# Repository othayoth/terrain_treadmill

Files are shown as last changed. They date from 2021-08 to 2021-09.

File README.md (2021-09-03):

# Terrain Treadmill 
This repository contains code being used to run the complex terrain treadmill in the [Terradynamics Lab](https://li.me.jhu.edu/) at Johns Hopkins University and accompanies publication ['A terrain treadmill to study small animal locomotion through large obstacles'](https://doi.org/10.1101/2021.08.31.458392)

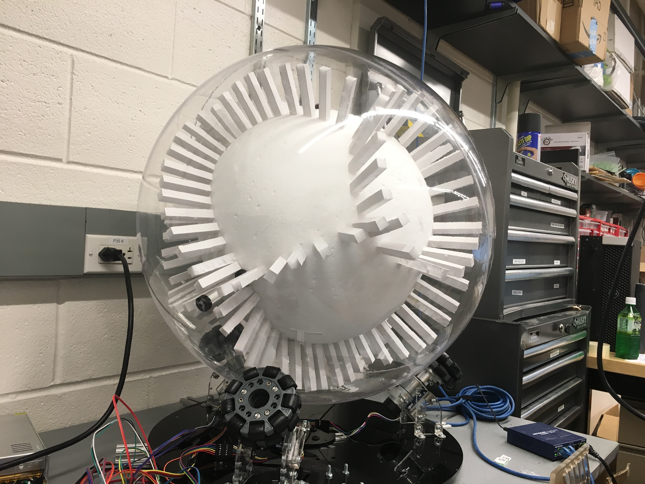
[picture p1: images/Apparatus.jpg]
Apparatus apparatus image


## Project Description
The purpose of this project was to develop a novel terrain treadmill to study Animal-Terrain Interaction During Locomotion in Complex Environments. This device allows for detailed study of cockroach dynamics and behavior over over large spatiotemporal scales.

### Table of Contents

* [Overview and Setup](#terrain-treadmill)
    * [Device Overview](#device-overview)
	* [Installation Instructions](#installation-instructions)
	* [Running the Device](#running-the-device)
	* [Device Tuning](#device-tuning)
  * [Data Analysis](#data-analysis)
	* [Maintenance](#maintenance)
	* [Parts List](#parts-list)
* [Nodes](./src#nodes)
* [Launch Files](./launch#launch-files)
* [Arduino Code](./Arduino#arduino-code)

## Device Overview

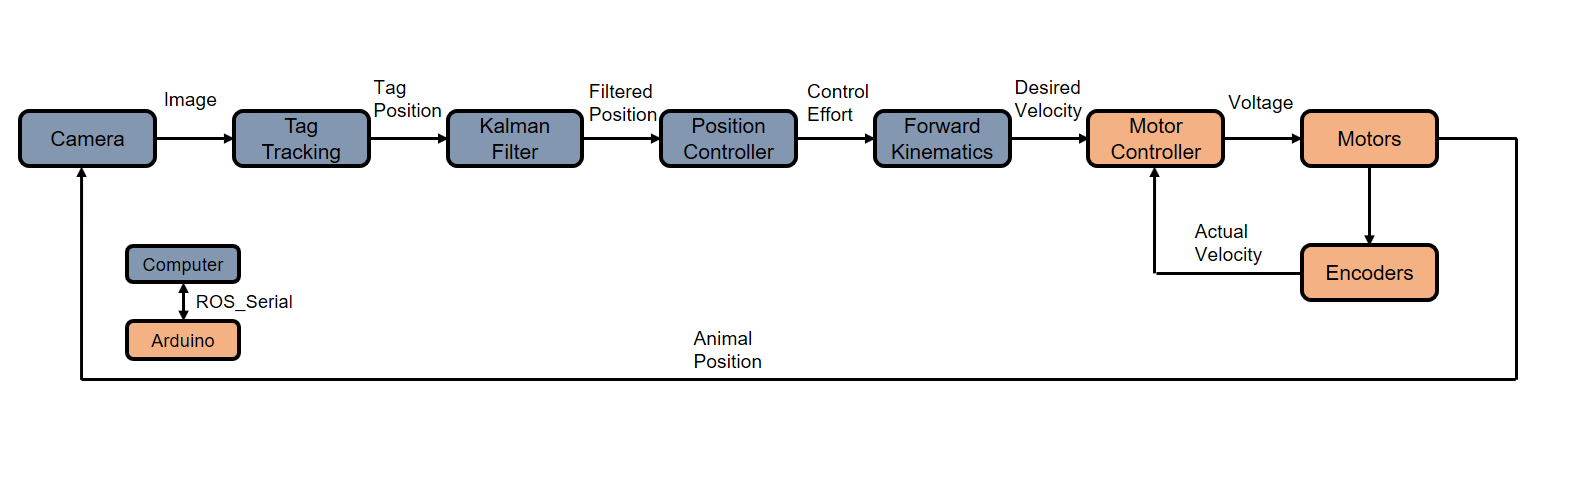
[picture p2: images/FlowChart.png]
FlowChart device flow chart

The terrain treadmill consists of two concentric spheres rigidly attached together. The animal moves through interchangeable terrain modules mounted on the inner sphere, and the transparent outer sphere allows its position to be tracked in real time. This information is then used to actuate the spheres via close-loop control, so that they rotate in the opposite direction in order to keep the animal on top.

The device uses a computer running ROS Indigo for image processing, filtering, and control. An Arduino is used to control the motors which actuate the device. To learn more about the ROS nodes being used to control the device, see the [node](./src) section. To learn more about the Arduino code, see the [Arduino](./Arduino) section.

## Installation Instructions
### ROS Package Install

First, make sure that ROS is installed and that you have a properly configured catkin [workspace](http://wiki.ros.org/catkin/Tutorials/create_a_workspace). Clone this project into your workspace using:
* `git clone git@github.com:TerradynamicsLab/terrain_treadmill.git`

This repository also has several dependencies on packages not yet released on `apt-get`. Install these packages using the same method as above:
* [aruco_ros](https://github.com/pal-robotics/aruco_ros): minimum version required 0.2.2
* [camera_base](https://github.com/KumarRobotics/camera_base)
* [flea3](https://github.com/KumarRobotics/flea3)

The remaining dependencies are listed in [CMakeLists.txt](./CMakeLists.txt) and can be installed normally using `apt-get`. Source the workspace `source devel/setup.bash` and make the package `catkin_make` to build the project.

### Hardware setup
An [Arduino Due](https://store.arduino.cc/usa/arduino-due) is used to interface with the three [DC Motors](https://www.pololu.com/product/2826) used to actuate the device. A circuit diagram for the project can be found [here](./images/Circuit.pdf). This repository contains the necessary libraries to compile to main [terrain_treadmill.ino](./Arduino/terrain_treadmill/terrain_treadmill.ino) sketch and upload it to the Arduino. Copy the [pid_lib](./Arduino/Libraries/pid_lib) and [ros_lib](./Arduino/Libraries/ros_lib) (generated using [rosserial](http://wiki.ros.org/rosserial)) libraries into your Arduino libraries folder. Then compile and upload `terrain_treadmill.ino` onto the device.

* Note: if you have trouble compiling the Arduino Code, see the Arduino [readme](./Arduino).

## Running the Device
To start the device, navigate to your workspace, source the correct environment variables, and launch [start.launch](./launch/start.launch)
* `cd [catkin_ws]`
* `source devel/setup.bash`
* `roslaunch terrain_treadmill start.launch`

This will start the device with the default settings. [Rqt](http://wiki.ros.org/rqt) is used for real-time data analysis and debugging.

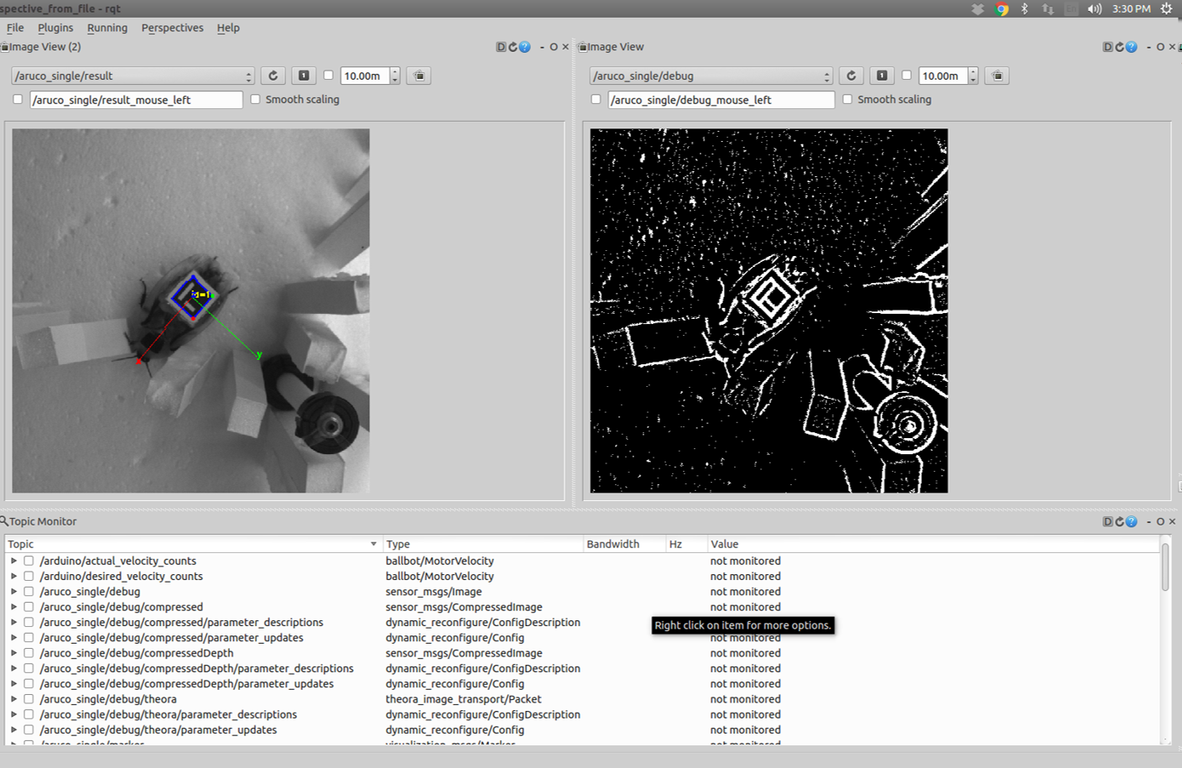
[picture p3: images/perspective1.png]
rqt1 rqt perspective 1


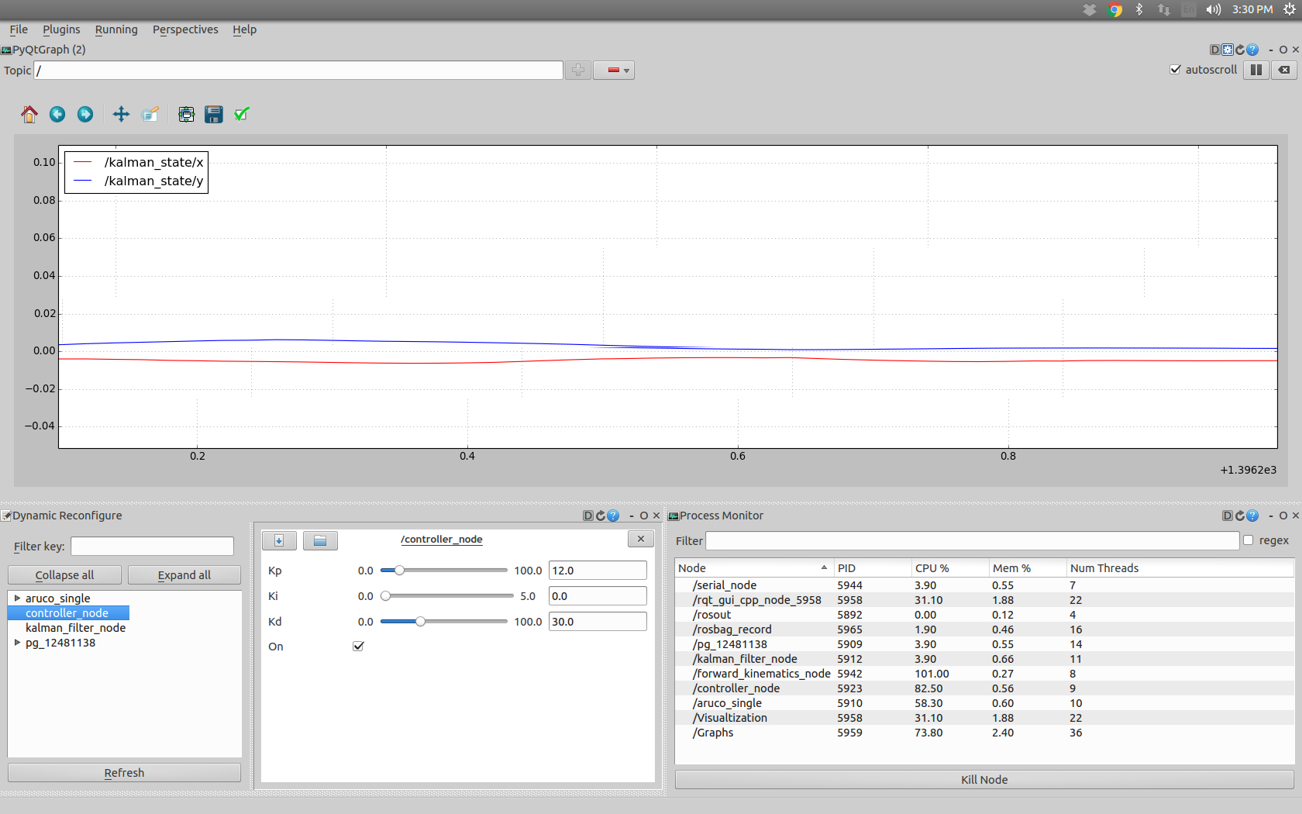
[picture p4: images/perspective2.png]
rqt2 rqt perspective 2


Various properties can be altered by specifying arguments at runtime. For example:
* `roslaunch terrain_treadmill start.launch record:=true`: records specified topics into a .bag file which is saved in the ~/.ros directory
* `roslaunch terrain_treadmill start.launch visualization:=false light_visualizations:=true`: starts the project in light visualization mode which hides debugging information

For more options, see [launch](./launch).

## Device Tuning

Tracking_Demo tracking demo

Several aspects of the device must be tuned in order to achieve optimum performance. These include:
* Low-Level Motor Controllers:
The Arduino uses three [PID Controllers](https://en.wikipedia.org/wiki/PID_controller) to match the desired velocity sent to the Arduino from the computer. These controllers are tuned to track the desired velocity as closely as possible while maintaining desired response characteristics (low overshoot, quick settling time, etc.). The [motor_test_node.py](./src/motor_test_node.py) node can be used to aid in the tuning of these controllers. See the [node readme](./src) for more information.

* Kalman Filter Gains:
A constant velocity model [kalman filter](https://en.wikipedia.org/wiki/Kalman_filter) is used to estimate the animal position when the tracking data becomes temporarily unavailable. Several aspects of the filter must be tuned for optimal performance. For this project, the most relevant parameter is the process covariance which can be tuned using dynamic reconfigure. For more information on the kalman filter, see the [node readme](./src).

* High-Level Controller:
A PID position controller is used to determine the desired control effort as a result of the animal's deviation from the center of the image frame. The PID gains from this controller can be tuned using dynamic reconfigure. For more information on this controller, see the [node readme](./src).

* Camera parameters:
Various camera parameters must be tuned in order to obtain good images for tracking. Camera placement, focus, lens size, and aperture are all hardware adjustments for this setup. Additionally, there are several parameters which can be adjusted in [flea3.launch](./launch/flea3.launch). These parameters can be tuned using dynamic reconfigure and then saved using the launch file.

  * Frame-rate: dictates how quickly the camera captures images. Note, higher frame rates do not necessarily result in better performance if Aruco tag detection cannot analyze images quickly enough. It is recommended to match the frame-rate to the frequency of Aruco tag detection at a given resolution.

  * Resolution: dictates the computational cost for Aruco tag detection. The smallest resolution that satisfies the other requirements is recommended. Aruco tag detection can be performed at ~50 Hz using a 688 x 700 image.

  * Shutter-Time: dictates how long shutter stays open for each image capture. Keep shutter-time low to reduce motion blur and improve tag detection. For this setup, a 5 ms shutter time produces good results.

  * For more information on tuning camera parameters, see [Guide to photography](https://i.redd.it/tq0zowda2shz.jpg).

  * Before use, the camera will also need to be calibrated to account for distortion. For information on how to calibrate the camera, see the [launch readme](./launch).

* Aruco Tracking Parameters:
[Aruco](https://www.uco.es/investiga/grupos/ava/node/26) is a tracking library which uses VR tags to determine tag locations in real-world coordinates. [Pal Robotics ROS implementation](https://github.com/pal-robotics/aruco_ros) of the library is used for this project. Assuming the camera parameters are set properly, there are several Aruco parameters which also must be adjusted for optimal performance. First, the markerID and size must be properly set in [aruco_marker_finder.launch](./launch/aruco_marker_finder.launch). The threshold parameters can then be adjusted using dynamic reconfigure. To permanently save adjustments, change the default values within your aruco_ros ArucoThreshold.cfg file. Note: this file is not located in the terrain_treadmill package.

## Data Analysis
Data can be recorded in a [rosbag](http://wiki.ros.org/rosbag) by running `roslaunch terrain_treadmill start.launch record:=true.` This results in a rosbag file containing being stored in your `~/.ros` directory. This bag can be played back for analysis. For more information on using rosbag to play back data, see [here](http://wiki.ros.org/rosbag/Commandline#play). Videos recorded in rosbag files can also be exported in your desired format. For information on exporting rosbag videos, see [here](http://wiki.ros.org/rosbag/Tutorials/Exporting%20image%20and%20video%20data). Rosbag files can also be imported directly to MATLAB using the [Robotics Systems Toolbox](https://www.mathworks.com/help/robotics/index.html). This package contains custom messages which will need to be imported to MATLAB using the [rosgenmsg](https://www.mathworks.com/help/robotics/ref/rosgenmsg.html) function which requires the [Robotics System Toolbox Interface for ROS Custom Messages](https://www.mathworks.com/matlabcentral/fileexchange/49810-robotics-system-toolbox-interface-for-ros-custom-messages).

## Maintenance
Acrylic hemispheres quickly build up finger prints, scuff marks, small scratches, and tape residue during normal use. DO NOT clean acrylic with regular towels. Use microfiber clothes to avoid scratching the surface. Use [acrylic cleaner](https://www.amazon.com/NOVUS-7100-Plastic-Polish-Kit/dp/B002UCYRZU) to help remove finger prints, dirt, and small scratches. Use [WD-40](https://www.amazon.com/WD-40-Multi-Use-Product-Multi-Purpose-Lubricant/dp/B0083V8H0I/ref=sr_1_1?s=automotive&ie=UTF8&qid=1504127919&sr=1-1&keywords=wd-40) to aid in the removal of tape residue.

## Parts List
* 1x [Arduino Due](https://store.arduino.cc/usa/arduino-due)
* 3x [DC Motor + Encoder](https://www.pololu.com/product/2826)
* 3x [DC Motor Driver](https://www.amazon.com/SainSmart-Stepper-Controller-Mega2560-Duemilanove/dp/B00AJGM37I)
* 1x [12V Power Supply](https://www.amazon.com/eTopxizu-Universal-Regulated-Switching-Computer/dp/B00D7CWSCG)
* 2x 24" Optically Clear Acrylic Hemisphere
* 1x 16" Styrofoam Ball
* 1x Tapped Plastic Rod + 2x screws
* 1x [Pointgrey Flea3 Camera](https://www.ptgrey.com/flea3-usb3-vision-cameras)
* 1x [16 mm lens](http://www.fujifilmusa.com/products/optical_devices/machine-vision/1-15-mp/cf16ha-1/)

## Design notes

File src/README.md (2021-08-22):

# Nodes

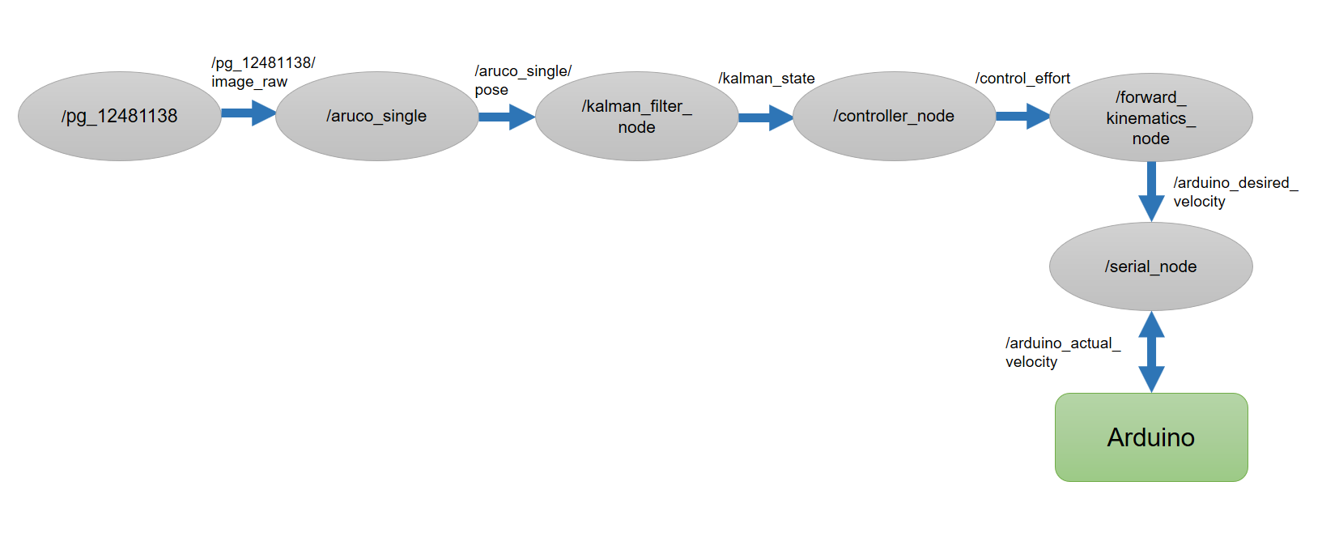
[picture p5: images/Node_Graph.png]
node graph simplified node graph


### Table of Contents
* [Overview and Setup](https://github.com/TerradynamicsLab/terrain_treadmill#terrain-treadmill)
* [Nodes](#nodes)
	* [/pg_12481138](#pg_12481138)
	* [aruco_single](#aruco_single)
	* [kalman_filter_node](#kalman_filter_node)
		* [tag_marker](#tag_marker)
		* [filter_marker](#filter_marker)
		* [tuning](#tuning)
	* [controller_node](#controller_node)
	* [forward_kinematics_node](#forward_kinematics_node)
	* [serial_node](#serial_node)
	* [motor_test_node](#motor_test_node)
* [Launch Files](../launch#launch-files)
* [Arduino Code](../Arduino#arduino-code)

## pg_12481138
This node publishes data from the camera used to track the Aruco tag located on the animal. It is started by [flea3.launch](../launch/flea3.launch). This node publishes several topics, the most relevant topics are:
* `/pg_12481138/camera_info` contains camera calibration data. It is used by the `aruco_single` node to convert tag position from pixels into real-world coordinates.
* `/pg_12481138/image_raw` contains the raw images output by the camera.
* `/pg_12481138/image_raw/compressed` contains compressed images output by the camera. Recording compressed images rather than raw images using rosbag results in smaller file sizes. Generally, all image topics in this package contain a corresponding compressed version. To view this topic using image_view, use: `rosrun image_view image_view image:=/pg_12481138/image_raw compressed`.

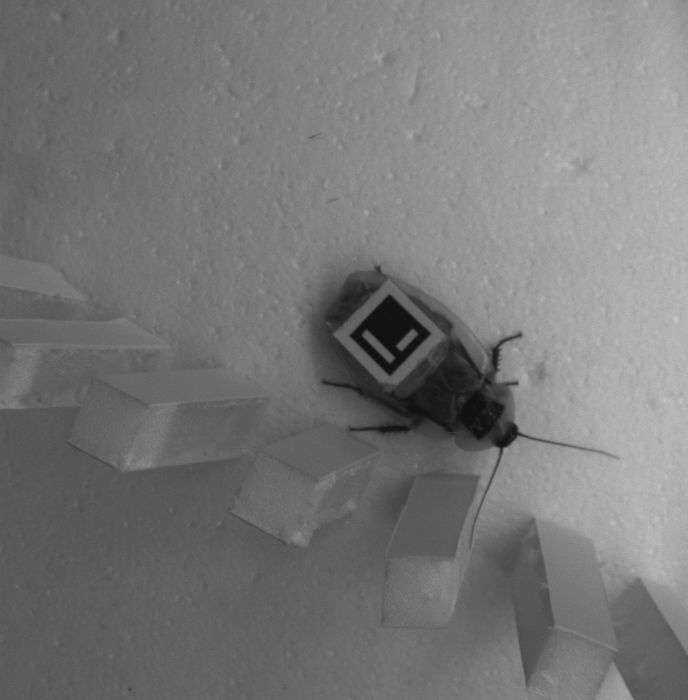
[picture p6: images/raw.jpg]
image_raw /pg_12481138/image_raw


## aruco_single
This node performs Aruco tag tracking. It is started by [aruco_marker_finder.launch](../launch/aruco_marker_finder.launch) It subscribes to `/pg_12481138/image_raw` and `/pg_12481138/camera_info` and uses this data to detect the tag position and convert it to real-world coordinates. This node publishes several useful topics:
* `/aruco_single/pose` contains position and orientation of Aruco tag using [geometry_msgs/Pose](http://docs.ros.org/api/geometry_msgs/html/msg/Pose.html) message.
* `/aruco_single/result` contains image displaying tag tracking result. Useful for tuning tracking and camera parameters.

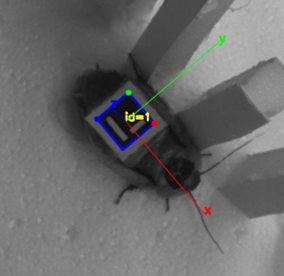
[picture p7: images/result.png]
result /aruco_single/result


* `/aruco_single/debug` contains binary image displaying result of image thresholding performed Aruco node. This image is used to tune the Aruco parameters discussed [here](https://github.com/TerradynamicsLab/terrain_treadmill#device-tuning).

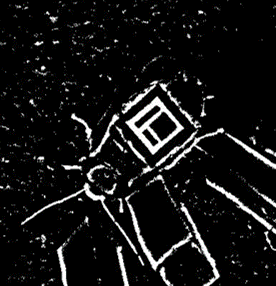
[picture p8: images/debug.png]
debug /aruco_single/debug


## kalman_filter_node
[kalman_filter_node.py](./kalman_filter_node.py) filters noisy position data from Aruco tag tracking. Furthermore, this node is used to predict tag location when the tag is temporarily obscured by obstacles. This makes the apparatus more reliable and less-prone to sudden impulses when tracking is inconsistent. This node is a constant velocity Kalman filter. To learn more about Kalman filters, start [here](https://en.wikipedia.org/wiki/Kalman_filter).

The node subscribes to the `aruco_single/pose` topic, performs filtering, and publishes the `kalman_state` topic at a [fixed frequency](./kalman_filter_node.py#L48) regardless of camera frame-rate. The filter first predicts a new state using previous state information and a constant velocity kinematic model.

```python

# Time Update (Prediction)
# ========================
# Project the state ahead
self.x = self.F*self.x

# Project the error covariance ahead
self.P = self.F*self.P*self.F.T + self.Q								

```

 Then, if new state information has been determined by the Aruco tracking node, it performs a correction (measurement) in which it uses measurement information to obtain a more accurate guess of the tag state as well as to influence future predictions.

```python
# Measurement Update (Correction)
# ===============================
# Compute the Kalman Gain
S = self.H*self.P*self.H.T + self.R
K = (self.P*self.H.T) * np.linalg.pinv(S)

# Update the estimate via z
Z = np.matrix([[self.posex, self.posey, self.yaw]]).T
y = Z - (self.H*self.x)
self.x = self.x + (K*y)

# Update the error covariance
self.P = (self.I - (K*self.H)) *self.P

 ```

 If no measurement information is available, it continues performing predictions until a limit is reached. After this limit, it uses measurements of zero to halt the apparatus motion until Aruco tracking information becomes available.

 ```python

 if self.missed_frames > 15:
 				##  Use zero as the measurement
 				self.posex = 0
 				self.posey = 0
 				self.yaw = 0

 				# Compute the Kalman Gain
 				S = self.H*self.P*self.H.T + self.R
 				K = (self.P*self.H.T) * np.linalg.pinv(S)

 				# Update the estimate via z
 				Z = np.matrix([[self.posex, self.posey, self.yaw]]).T
 				y = Z - (self.H*self.x)
 				self.x = self.x + (K*y)

 				# Update the error covariance
 				self.P = (self.I - (K*self.H)) *self.P

 ```

 The filter's process covariance can be tuned using rqt_reconfigure to alter the sensitivity to new measurements. The tag_marker and filter_marker nodes discussed below can be helpful in tuning the filter parameters to obtain the desired response.

 #### tag_marker

 [tag_marker.py](./tag_marker.py) subscribes to Aruco tag information from the `/aruco_single/pose` topic. It uses this data to publish an [Rviz](http://wiki.ros.org/rviz) marker on the `/tag_marker` topic.

 #### filter_marker

 [filter_marker.py](./filter_marker.py) subscribes to filter information on the `/kalman_state` topic. It uses this data to publish an Rviz marker on the `/filter_marker topic`

 #### tuning
[Rviz](http://wiki.ros.org/rviz) is a ROS package useful for data visualization. It subscribes to [Rviz Markers](http://wiki.ros.org/rviz/DisplayTypes/Marker) and displays them in a 3-D environment. These markers can be used to tune the Kalman filter process covariance (or other parameters) using rqt_reconfigure. To start the apparatus in the proper configuration for tuning, set the Rviz argument to true: `roslaunch terrain_treadmill start.launch Rviz:=true`.

[Examples]

## controller_node

[controller_node.py](./controller_node.py) is the high level position PID controller for the device. This node subscribes to the `/kalman_state` topic containing position information about the tag located on the animal body. The 2-D deviation from center (x,y) is used as the error for the controller. The orientation (theta) is not considered. The error is fed into a PID controller and control effort is calculated:

```python
def PID_Controller(self, msg):
    # Calculate Error
    self.Ex = msg.x
    self.Ey = msg.y
    # self.Et = msg.theta

    # Calculate Integral Error
    self.Exint = self.Exint + self.Ex
    self.Eyint = self.Eyint + self.Ey
    # self.Etint = self.Etint + self.Et

    # Calculate Derivative Error
    self.Exdot = self.Ex - self.Exold
    self.Eydot = self.Ey - self.Eyold
    # self.Etdot = self.Et - self.Etold

    # Update Previous Error
    self.Exold = self.Ex
    self.Eyold = self.Ey
    # self.Etold = self.Et

    # Calculate Control Effort
    self.controlEffort.Ux = self.Kp*self.Ex + self.Ki*self.Exint + self.Kd*self.Exdot
    self.controlEffort.Uy = self.Kp*self.Ey + self.Ki*self.Eyint + self.Kd*self.Eydot
    self.controlEffort.Ut = 0.0 #self.Kp*self.Et + self.Ki*self.Etint + self.Kd*self.Etdot
    self.controlEffort.header.stamp = rospy.Time.now()
```

 This control effort is published on the `/control_effort` topic. When the tag is within 3 mm of the center of the frame, no control effort is used. The PID gains are tunable using rqt_reconfigure. The controller can also be turned on/off using rqt_reconfigure.

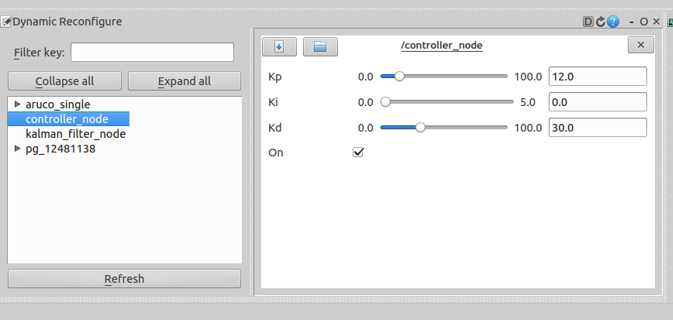
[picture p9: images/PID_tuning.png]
PID Tuning


## forward_kinematics_node

[forward_kinematics_node.py](./forward_kinematics_node.py) subscribes to the `/control_effort` containing real-world control effort information (x, y, theta) and converts this information into the required motor velocities for the three motors which will cause the ball to rotate in the desired trajectory. These velocities are then converted from `rad/s` into `encoder counts/controller interrupt` and published on the `/arduino/desired_velocity_counts` topic.

The forward kinematics for this structure were obtained from this [paper](http://ieeexplore.ieee.org/document/5152324/). They are given by:

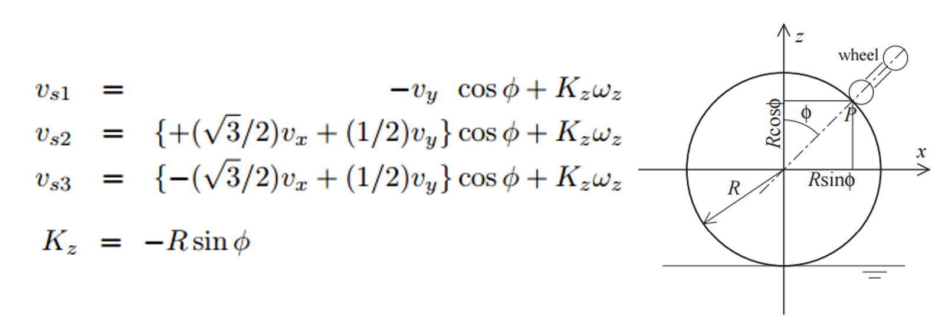
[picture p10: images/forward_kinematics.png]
forward_kinematics


## serial_node

The serial node is started by [serial.launch](../launch/serial.launch). This node is responsible for maintaining communication between ROS and the Arduino. It subscribes to the `/arduino/desired_velocity_counts` topic and sends this data to the Arduino over the computer's serial port. It also receives the `/arduino/actual_velocity_counts` information over the same serial port and publishes this topic.

## motor_test_node

[motor_test_node.py](./motor_test_node.py) can be used to tune the PID controllers being used to control the DC motors. The node uses rqt_reconfigure to send desired velocities to each motor in counts. The desired/actual velocities can be plotted to aid in the tuning of the controllers.
* `rosrun terrain_treadmill motor_test_node.py` to start the node
* `rosrun rqt_reconfigure rqt_reconfigure` to startup rqt_reconfigure
* `rosrun rqt_plot rqt_plot` to start rqt_plot. Add `/arduino/actual_velocity_counts` and `/arduino/desired_velocity_counts` and then configure to visualize results

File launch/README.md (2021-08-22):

# Launch Files

### Table of Contents

* [Overview and Setup](../#terrain-treadmill)
* [Nodes](../src#nodes)
* [Launch Files](#launch-files)
	* [start](#start)
	* [aruco_marker_finder](#aruco_marker_finder)
	* [flea3](#flea3)
	* [serial](#serial)
* [Arduino Code](../Arduino#arduino-code)

## start
[start.launch](./start.launch) is used to startup the entire apparatus. This launch file allows the apparatus to be started without certain nodes for debugging purposes (see launch file for options).

The file can also be used to setup data collection for the device. Setting the `record` arg to true causes a rosbag to be recorded. By default, this file will be saved in the `~/.ros` directory. To change which topics are recorded, add or delete them from the [arguments list](./start.launch#L68-L69).

For more information on using rosbag, see the [package documentation](http://wiki.ros.org/rosbag). For more information on using rosbag to playback data using command-line arguments, see [here](http://wiki.ros.org/rosbag/Commandline).

## aruco_marker_finder
[aruco_marker_finder.launch](./aruco_marker_finder.launch) is used to start the [simple_single](https://github.com/pal-robotics/aruco_ros/blob/indigo-devel/aruco_ros/src/simple_single.cpp) node from the [aruco_ros package](https://github.com/pal-robotics/aruco_ros)  with the proper settings for tag detection. Before using, this launch file confirm that:
* The [markerId](./aruco_marker_finder.launch#L3) is properly specified. To generate new markers, modify [this url](http://terpconnect.umd.edu/~jwelsh12/enes100/marker.html?id=1&size_mm=70&padding_mm=5).
* The [markerSize](./aruco_marker_finder.launch#L4) has been measured and specified.
* The [camera topics](./aruco_marker_finder.launch#L11-L12) have been properly remapped.

## flea3
[flea3.launch](./flea3.launch) is used to start a Point Grey [Flea3 camera](https://www.ptgrey.com/support/downloads/10120) using the [flea3_single_node](https://github.com/KumarRobotics/flea3/tree/master/src/single) from the [flea3](https://github.com/KumarRobotics/flea3/tree/master/src) package. This launch file allows the camera parameters to be set to desired values. Camera tuning is disucssed in the main package [readme](../README.md#terrain-treadmill). After tuning, this launch file can also be used to calibrate the camera. Print out a [calibration board](http://wiki.ros.org/camera_calibration/Tutorials/MonocularCalibration?action=AttachFile&do=view&target=check-108.pdf) and measure the size of one of the squares. Then, calibrate the camera by running:
* `roslaunch terrain_treadmill flea3.launch calib:=true size:=8x6 square:=[measured square size]`

After, overwrite the old [calibration file](../config/camera.yaml) with your new calibration. For more information on using ROS to calibrate your camera, see the [camera_calibration](http://wiki.ros.org/camera_calibration/Tutorials/MonocularCalibration) package.

## serial
[serial.launch](./serial.launch) is used to start a serial communication stream between ROS and the Arduino. In order to start the serial stream, the serial [port](./serial.launch#L3) and [baud](./serial.launch#L4) must be properly specified. Specifically, the baud must match the [Arduino](../Arduino/terrain_treadmill/terrain_treadmill.ino#L12). Note, for the Arduino Due, the max serial rate is `115200`, but the default rate has proven to be more reliable. If higher serial rates are required, consider switching to a different microcontroller or communication protocol.

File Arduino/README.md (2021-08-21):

# Arduino Code

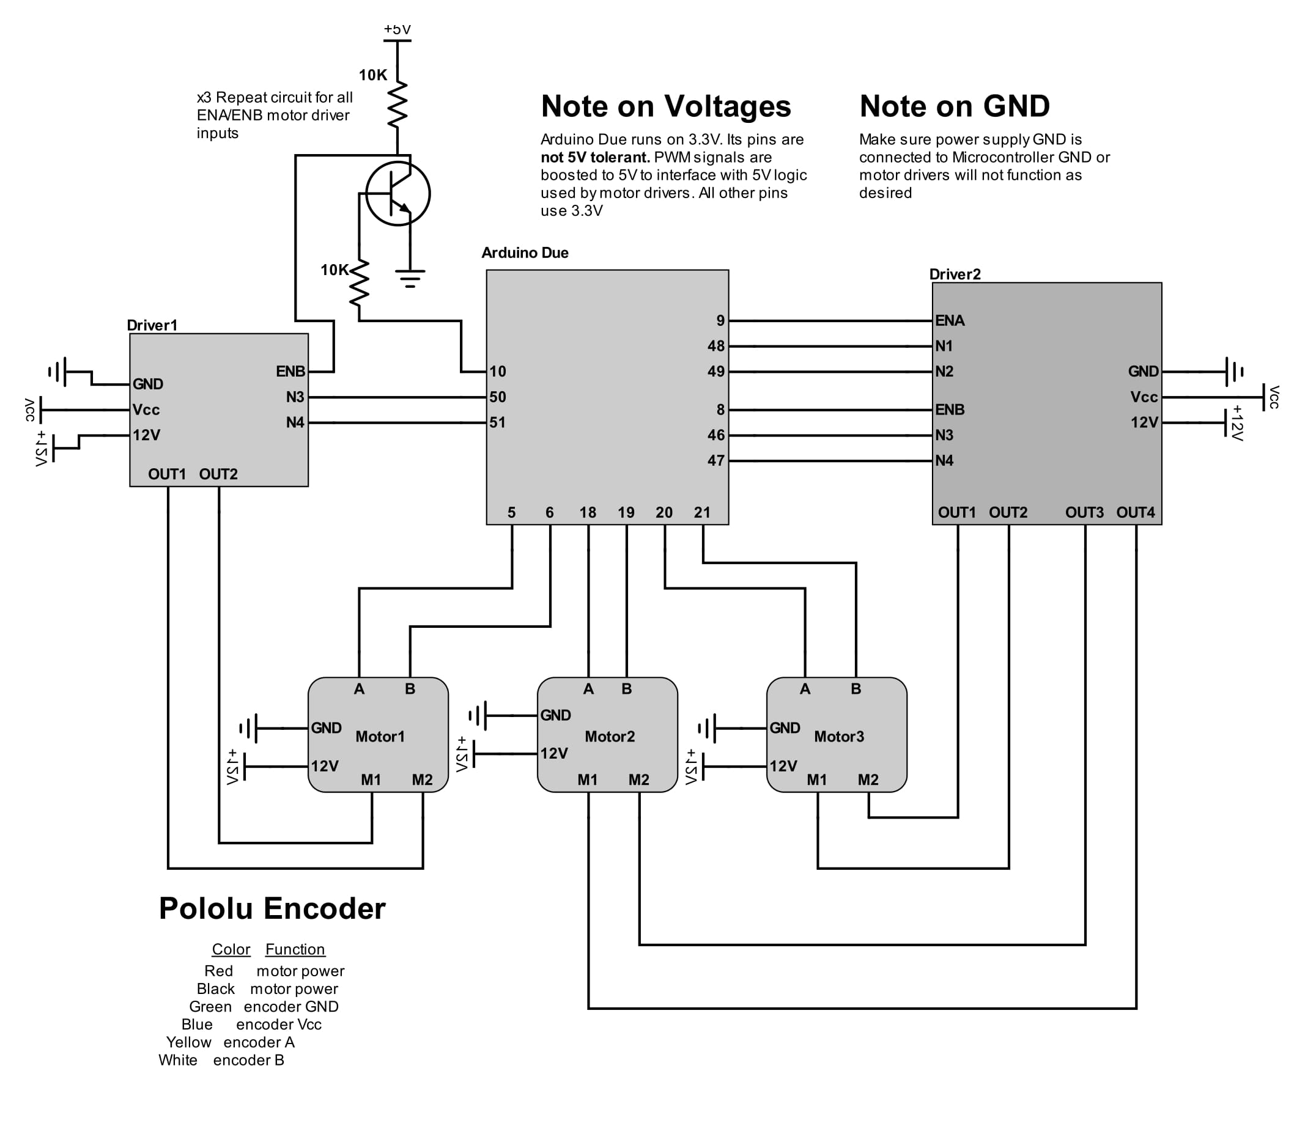
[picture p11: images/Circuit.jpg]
circuit diagram


### Table of Contents

* [Overview and Setup](#terrain-treadmill)
* [Nodes](../src#nodes)
* [Launch Files](../launch#launch-files)
* [Arduino Code](#arduino-code)
	* [Main](#main)
	* [Libraries](#libraries)
	    * [ROS Interface Library](#ros-interface-library)
	    * [Motor Control Library](#motor-control-library)
	    	* [Encoder](#encoder)
	    	* [Controller](#controller)
	    	* [Motors](#motors)
	    	* [Utilities](#utilities)
	    	* [Timer](#timer)

## Main

[terrain_treadmill.ino](./terrain_treadmill/terrain_treadmill.ino) is the main sketch running on the Arduino. It sets up ROS Communication, initializes the motor controllers, and receives/sends desired/actual motor velocities to ROS.

## Libraries

### ROS Interface Library
[ros_lib](./Libraries/ros_lib) contains the files required to use [rosserial](http://wiki.ros.org/rosserial) to communicate with the Arduino. If you're having trouble getting the sketch to compile after following the instructions in [Hardware setup](), try reinstalling ros_lib in your Arduino sketchbook by sourcing your workspace and then [Install ros_lib into the Arduino Environment](http://wiki.ros.org/rosserial_arduino/Tutorials/Arduino%20IDE%20Setup). NOTE, when using this library with an Arduino Due, manually change `Serial1` to `Serial` in [ArduinoHardware.h](./Libraries/ros_lib/ArduinoHardware.h#L68) or the Arduino will not connect with ROS.

### Motor Control Library
[pid_lib](./Libraries/pid_lib) is a custom C library for velocity control of 3 DC motors with encoders using PID control. The library files are organized as follows. For more information on an individual file, check the comments. This library can easily be adapted to use more/less motors or different hardware.

#### Encoder

[Encoder.cpp](./Libraries/pid_lib/Encoder.cpp), [Encoder.h](./Libraries/pid_lib/Encoder.h)

These files contain the functions which are used to interpret the quadrature encoder waveforms to determine motor position and velocity. The encoder signals cause rising-edge interrupts on the Arduino. The [interrupt service routines](./Libraries/pid_lib/Encoder.cpp#L216-L298) then add/subtract counts to the position totals. For this implementation, the full resolution of the encoder is not utilized in interest of simplifying the computational cost. Therefore, the total encoder resolution should be divided by four to obtain the actual resolution. The [filtered_velocity](./Libraries/pid_lib/Encoder.cpp#L193-L214) function uses a moving average of size n (set in [terrain_treadmill.ino](./terrain_treadmill/terrain_treadmill.ino#L22)) to get a less noisy estimate of the velocity at any time.  

#### Controller

[Controller.cpp](./Libraries/pid_lib/Controller.cpp), [Controller.h](./Libraries/pid_lib/Controller.h)

These files contain the fixed frequency PID controller used to control the motors to match their desired velocities. A [timer based interrpt](./Libraries/pid_lib/Controller.cpp#L26) is used to trigger the controller to update motor voltages at a fixed frequency. The actual positions/velocities are [read](./Libraries/pid_lib/Controller.cpp#L46-L48) by the controller and [compared](./Libraries/pid_lib/Controller.cpp#L50-L52) to the desired values. Then, the controller determines the [desired effort](./Libraries/pid_lib/Controller.cpp#L142-L146) based on the error between the two. If the effort is negative, the motor direction is [flipped](./Libraries/pid_lib/Controller.cpp#L166-L174). Max control effort corresponds with a [full byte](./Libraries/pid_lib/Controller.cpp#L177-L180) (255).

#### Motors

[Motors.cpp](./Libraries/pid_lib/Motors.cpp), [Motors.h](./Libraries/pid_lib/Motors.h)

These files contain the necessary functions for interfacing with the motor drivers. If you are using a different motor driver, update the [motor_setup](./Libraries/pid_lib/Motors.cpp#L17-L39), [setPWM](./Libraries/pid_lib/Motors.cpp#L42-L62), and [motor_direction](./Libraries/pid_lib/Motors.cpp#L65-L105) functions as necessary.

#### Utilities

[Utilities.cpp](./Libraries/pid_lib/Utilities.cpp), [Utilities.h](./Libraries/pid_lib/Utilities.h)

These files contain the operating mode for the motor controllers. The only relevant operating mode for this project is VELOCITY_HOLD which turns on the velocity PID controller.

#### Timer

[DueTimer.cpp](./Libraries/pid_lib/DueTimer.cpp)/[DueTimer.h](./Libraries/pid_lib/DueTimer.h)

Contains code which implements timer-based interrupts for Arduino Due. This library was written by [ivanseidel](https://github.com/ivanseidel/DueTimer). Libraries for Arduino Uno/Mega can be found [here](https://playground.arduino.cc/Code/Timer1).

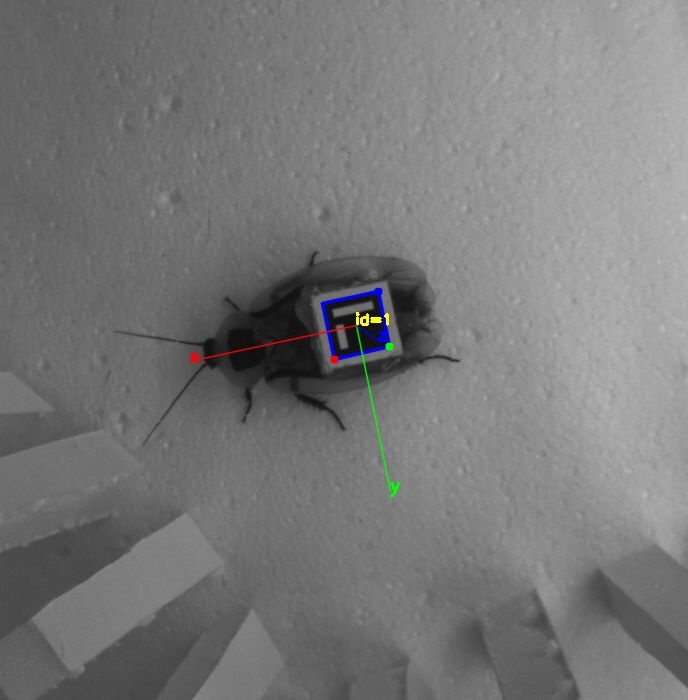
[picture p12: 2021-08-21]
images/tracking_snapshot.jpg

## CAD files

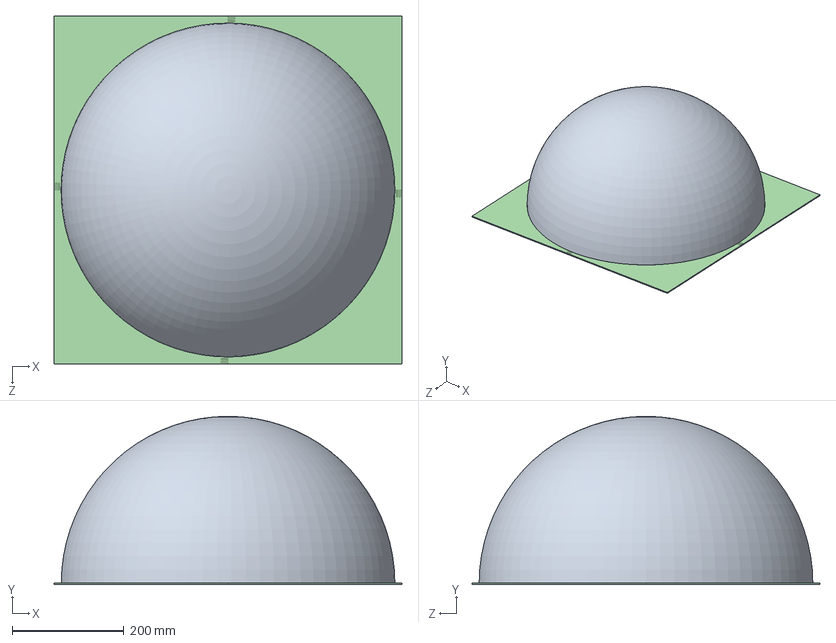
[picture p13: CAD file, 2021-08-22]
CAD/Hemispheres/Support/Support.SLDASM
622.3 x 301.0 x 622.3 mm
Hemisphere
Side1
Side2
Fixture x 4

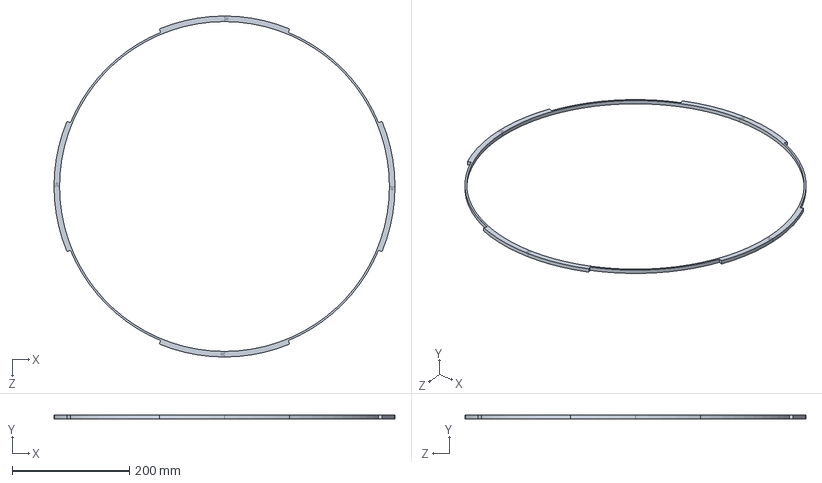
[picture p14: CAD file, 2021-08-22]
CAD/Hemispheres/Inner.SLDASM
582.4 x 6.35 x 582.4 mm
Inner_Connector x 4

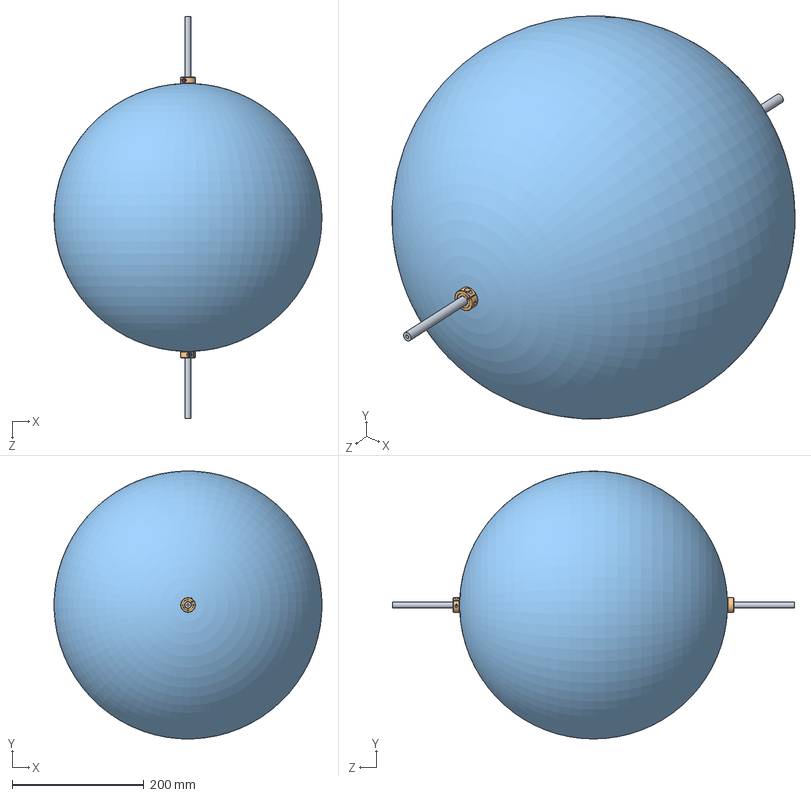
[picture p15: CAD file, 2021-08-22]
CAD/Shaft/ShaftAssembly.SLDASM
406.2 x 406.2 x 609.6 mm
Shaft
6435K130_ONE-PIECE CLAMP-ON SHAFT COLLAR x 2
InnerBall

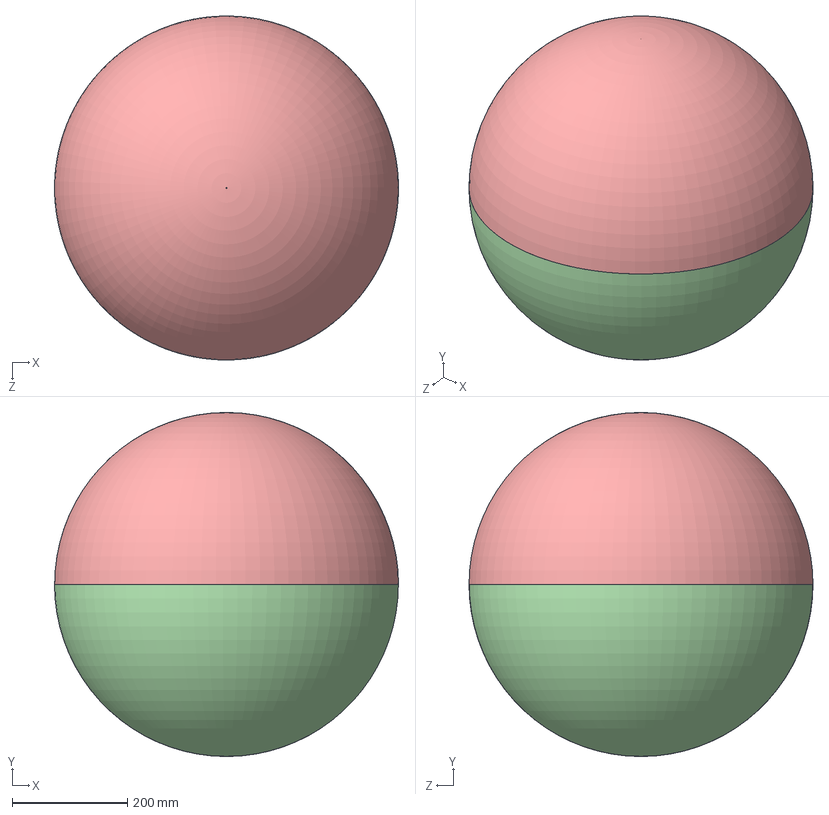
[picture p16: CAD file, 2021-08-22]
CAD/Hemispheres/Hemishere_Assem.SLDASM
596.9 x 596.9 x 596.8 mm
Inner_Connector x 4
Outer_Connector x 4
Ring x 8
Bottom
Top

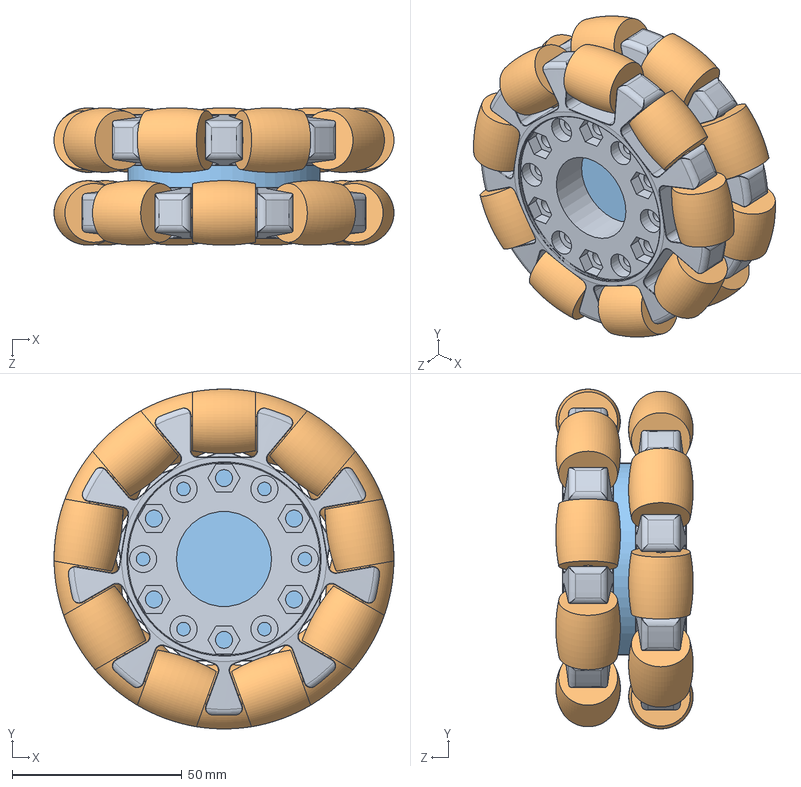
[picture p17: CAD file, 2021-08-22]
CAD/omniwheel_complete.SLDASM
100.0 x 100.0 x 40.4 mm
omniwheel_1 x 2
subwheel x 18
spacer

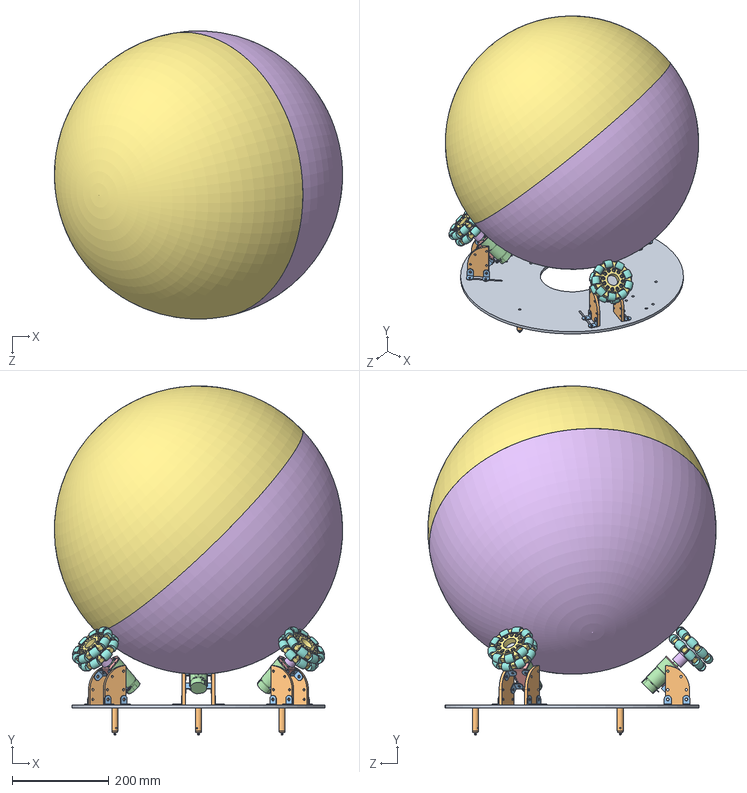
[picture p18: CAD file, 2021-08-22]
CAD/Ballbot_Assembly.SLDASM
596.5 x 722.5 x 596.5 mm
Base
Adjustable_Angle x 6
AngleBracket x 24
Motor x 3
Geared Motor Bracket x 3
Hub x 3
omniwheel_1 x 6
subwheel x 54
spacer x 3
94033A432_MALE-FEMALE THRDED ROUND STANDOFF x 3
Bottom
Top
Shaft
6435K130_ONE-PIECE CLAMP-ON SHAFT COLLAR x 2
InnerBall

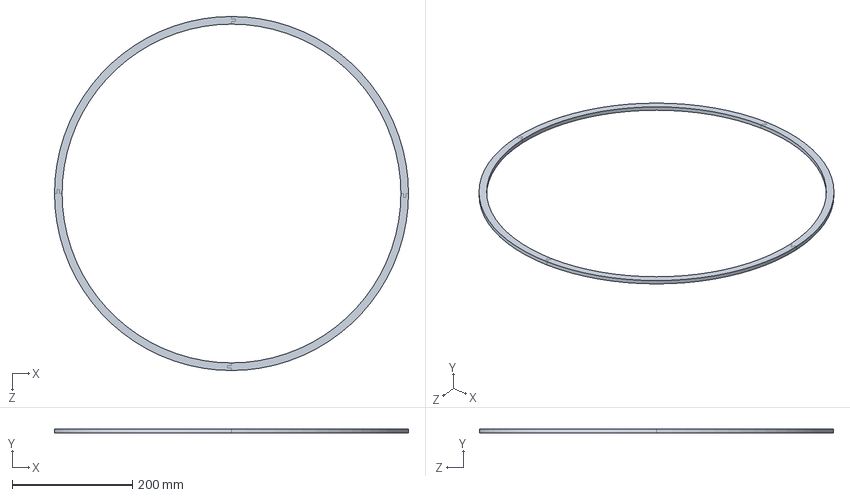
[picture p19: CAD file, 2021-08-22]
CAD/Hemispheres/Ring_Connected.SLDASM
588.8 x 6.35 x 588.8 mm
Ring x 4

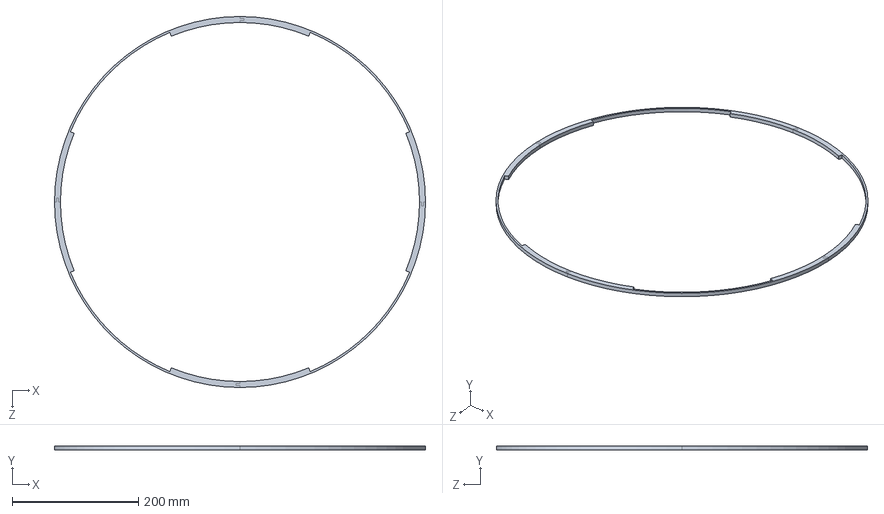
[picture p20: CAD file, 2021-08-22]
CAD/Hemispheres/Outer.SLDASM
588.8 x 6.35 x 588.8 mm
Outer_Connector x 4

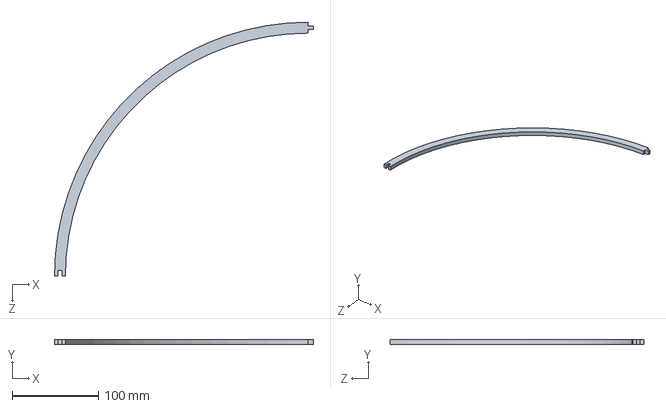
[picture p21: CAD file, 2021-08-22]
CAD/Hemispheres/Ring.SLDPRT
300.7 x 6.35 x 294.4 mm

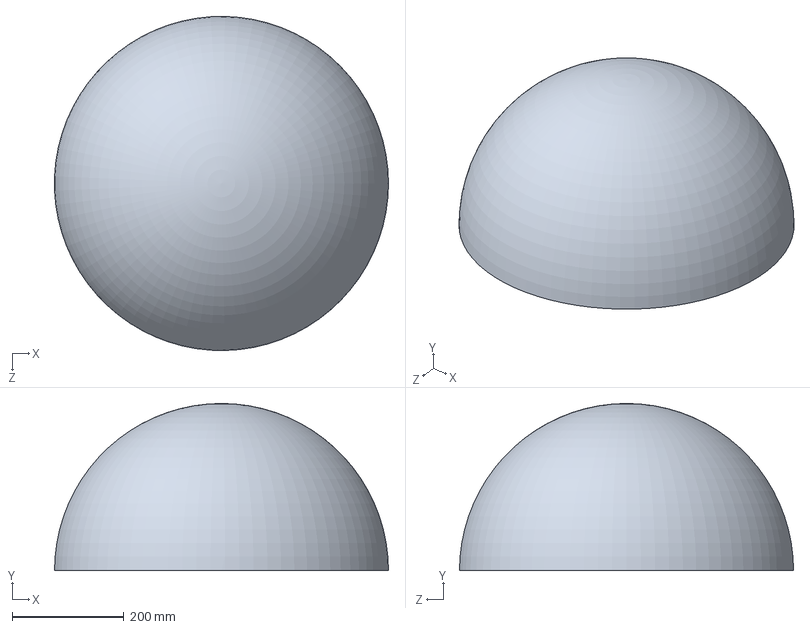
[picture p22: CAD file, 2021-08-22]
CAD/Hemispheres/Support/Hemisphere.SLDPRT
596.6 x 298.4 x 596.8 mm

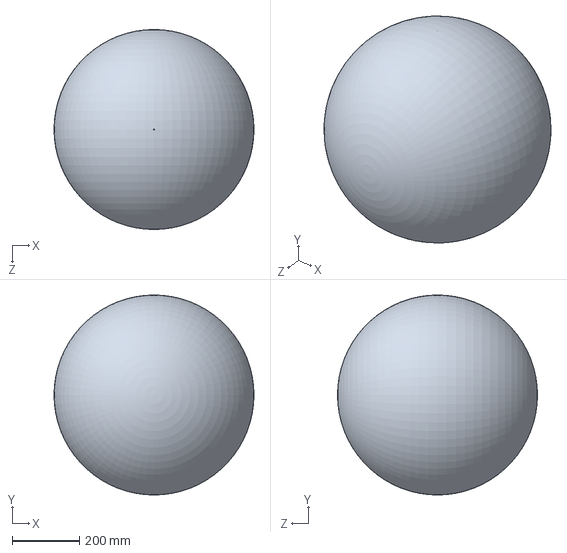
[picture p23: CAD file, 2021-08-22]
CAD/Outer_Ball_Big.SLDPRT
596.9 x 596.9 x 596.9 mm

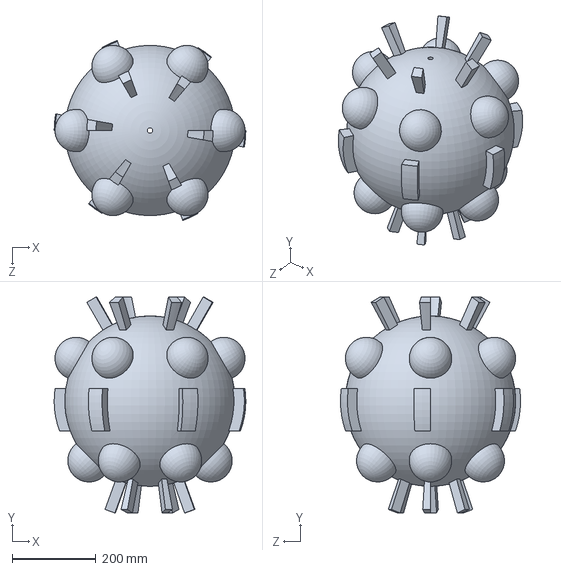
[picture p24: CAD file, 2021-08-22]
CAD/Shaft/InnerBall.SLDPRT
457.1 x 515.2 x 429.6 mm

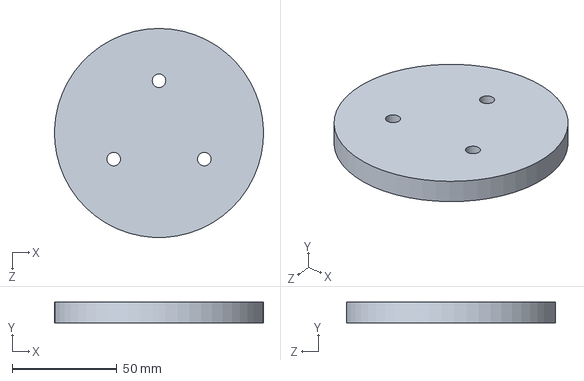
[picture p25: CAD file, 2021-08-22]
CAD/Circle_Support.SLDPRT
100.0 x 10.0 x 100.0 mm

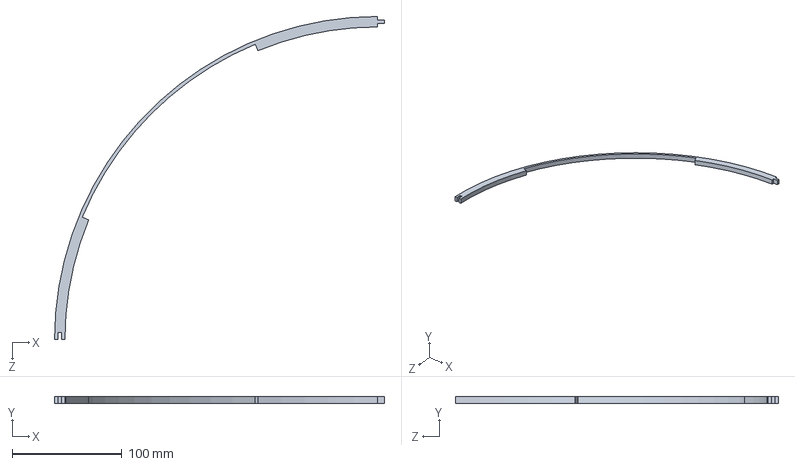
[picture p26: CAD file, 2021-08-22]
CAD/Hemispheres/Outer_Connector.SLDPRT
300.7 x 6.35 x 294.4 mm

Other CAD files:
CAD/Shaft/Shaft.SLDPRT
CAD/Hemispheres/Support/Side2.SLDPRT
CAD/spacer.SLDPRT
CAD/Hemispheres/Fixture.SLDPRT
CAD/94033A432_MALE-FEMALE THRDED ROUND STANDOFF.SLDPRT
CAD/Adjustable_Angle.SLDPRT
CAD/AngleBracket.SLDPRT
CAD/Base.SLDPRT
CAD/Circle_Support_Cut.SLDDRW
CAD/Geared Motor Bracket.SLDPRT
CAD/Hemispheres/Bottom.SLDPRT
CAD/Hemispheres/Fixture_LaserCut.SLDDRW
CAD/Hemispheres/Inner_Ball.SLDPRT
CAD/Hemispheres/Inner_Connector.SLDPRT
CAD/Hemispheres/Rings_LaserCut.SLDDRW
CAD/Hemispheres/Rings_LaserCut2.SLDDRW
CAD/Hemispheres/Rings_LaserCut3.SLDDRW
CAD/Hemispheres/Support.SLDPRT
CAD/Hemispheres/Support/47065T239_ALUMINUM T-SLOTTED FRAMING EXTRUSION.SLDPRT
CAD/Hemispheres/Support/AddHoles_LaserCut.SLDDRW
CAD/Hemispheres/Support/Side1.SLDPRT
CAD/Hemispheres/Support/Support_LaserCut.SLDDRW
CAD/Hemispheres/Through Rod.SLDPRT
CAD/Hemispheres/Top.SLDPRT
CAD/Hub.SLDPRT
CAD/Motor.SLDPRT
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

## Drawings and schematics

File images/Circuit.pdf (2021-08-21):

# Note on Voltages

# Note on GND

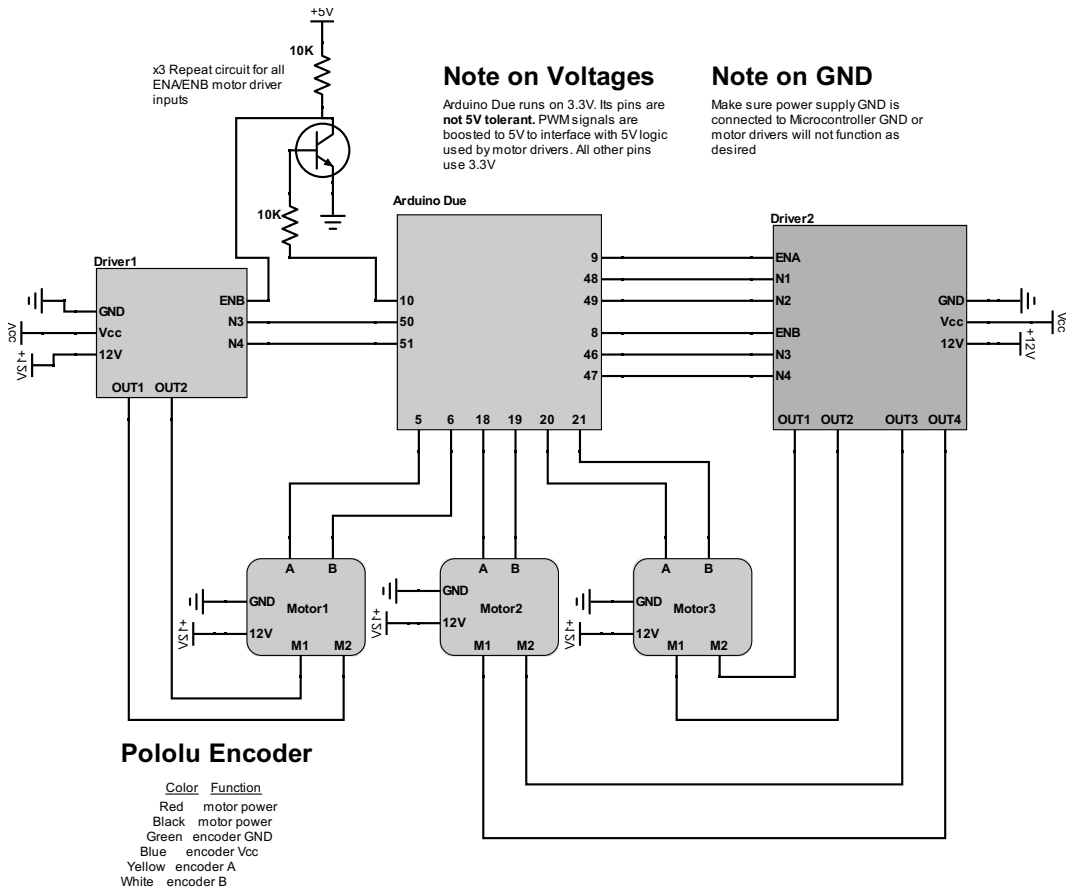
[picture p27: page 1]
Arduino Due; Motor1; GND; Motor2; Motor3; Driver1; Vcc; ENB; OUT1 OUT2; Driver2; ENA; OUT3 OUT4; Pololu Encoder; Red; motor power; Blue; encoder Vcc

x3 Repeat circuit for all
ENA/ENB motor driver
inputs

Arduino Due runs on 3.3V. Its pins are
not 5V tolerant. PWM signals are
boosted to 5V to interface with 5V logic
used by motor drivers. All other pins
use 3.3V

Make sure power supply GND is
connected to Microcontroller GND or
motor drivers will not function as
desired

Color Function
Black motor power
Green encoder GND
Yellow encoder A
White encoder B

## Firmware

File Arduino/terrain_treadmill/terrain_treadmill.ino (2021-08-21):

// ROS Utilities
#include <ros.h>               // ROS serial interface
#include <terrain_treadmill/MotorVelocity.h>

// Utilities from my library
#include <Encoder.h>
#include <Utilities.h> 
#include <Controller.h>
#include <Motors.h>

// Definitions
#define BAUD 57600
#define MOTOR1 1
#define MOTOR2 2
#define MOTOR3 3

// Parameters
#define ControllerFreq 200
#define Kp 400
#define Ki 2
#define Kd 400
#define SampleNumber 10

ros::NodeHandle nh;
terrain_treadmill::MotorVelocity vel_msg;

// Publisher publishes actual velocity information from motor encoders
ros::Publisher vel_pub("arduino/actual_velocity_counts", &vel_msg);

// Funcion called each time a new velocity command is recieved
void vel_cb( const terrain_treadmill::MotorVelocity& vel_in)
{
  // Set desired velocities for controller
  set_desired_velocity(vel_in.w1,MOTOR1);
  set_desired_velocity(vel_in.w2,MOTOR2);
  set_desired_velocity(vel_in.w3,MOTOR3);

  // Publish actual velocity information
  vel_msg.w1 = get_velocity(MOTOR1);
  vel_msg.w2 = get_velocity(MOTOR2);
  vel_msg.w3 = get_velocity(MOTOR3);
  vel_pub.publish( &vel_msg );
}

// Subscriber subcribes to velocity commands from Computer
ros::Subscriber<terrain_treadmill::MotorVelocity> vel_sub("/arduino/desired_velocity_counts", &vel_cb );

void setup()
{
  // Initialize hardware
  noInterrupts();
  encoder_setup(SampleNumber);      // Setup encoder pins/interrupts, set velocity moving average sample number
  set_gains(Kp,Ki,Kd);              // Set motor controller gains
  controller_setup(ControllerFreq); // Start fixed frequency controller interrupt
  motor_setup();                    // Setup motor control pins          
  interrupts();
  
  // Initialize ROS communication
  nh.getHardware()->setBaud(BAUD);
  nh.initNode();
  nh.subscribe(vel_sub);
  nh.advertise(vel_pub);
  
  // Start velocity control mode
  setMODE(VELOCITY_HOLD);
}

void loop()
{ 
  nh.spinOnce();  // Check for callbacks
  delayMicroseconds(1);
}
